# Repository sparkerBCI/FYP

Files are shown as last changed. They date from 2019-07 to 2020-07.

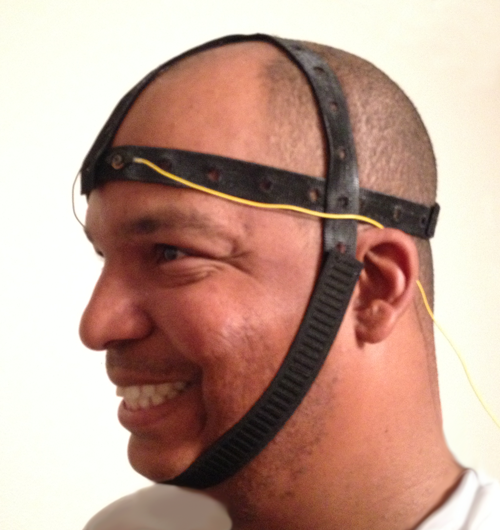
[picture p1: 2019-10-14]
Documentation/Report/Pictures/headstrap.png

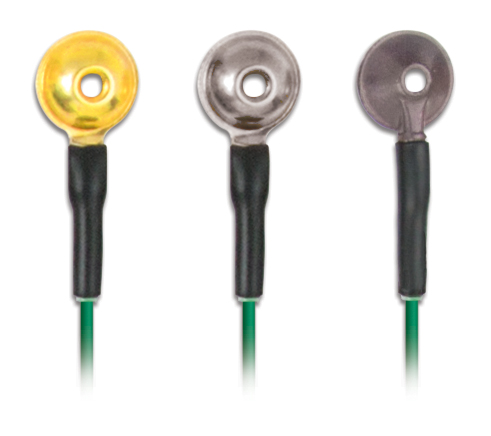
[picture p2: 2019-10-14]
Documentation/Report/Pictures/grass_stamped_eeg_cup_electrodes.jpg

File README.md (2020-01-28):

# Brain Computer Interface Controlled, 3-D Printed Prosthetic Hand

This is an Electrical Engineering Final   Year Project by Samuel Parker, from the University of Newcastle.

### Scope
The project will attempt to conduct a real time frequency analysis of on-line EEG data. The frequency content will then be classified into "Hand Open" or "Hand Closed" using an appropriate classification algorithm. Once classified, the state will be used to control the servos in the 3D printed prosthetic hand. The goal of the project is to achieve realtime, neurally controlled grasping.

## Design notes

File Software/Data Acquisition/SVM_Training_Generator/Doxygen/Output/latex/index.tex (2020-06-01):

\DoxyHorRuler{0}

\begin{DoxyAuthor}{Author}
Sam Parker 
\end{DoxyAuthor}
\begin{DoxyVersion}{Version}
0.\+03
\end{DoxyVersion}
\hypertarget{index_intro_sec}{}\doxysection{Introduction}\label{index_intro_sec}
This is the software for the Sparker Wireless E\+EG Data Acquisition System. It was developed by Sam Parker as part of his Electrical Engineering Final Year Project at the University of Newcastle, Australia. This software contains interface functions to set-\/up, configure, and operate a Texas Instruments A\+D\+S1299 E\+EG Analog Front End device. It then pipes the data to a serial port (U\+SB or Bluetooth).\hypertarget{index_mech}{}\doxysection{Mechanics}\label{index_mech}
The software is relatively simple. It instantiates a Pin\+\_\+\+Map, which tells the device how the pins are mapped. If this software is being run on a board other than the Sparker Data Acquisition System, you need to check the Pin\+\_\+\+Map is still correct. It then uses the Pin\+\_\+\+Map to communicate with the A\+D\+S1299 over an S\+PI interface. The device is configured for the Sparker Data Acquisition board, so if it is to be used with a different recording montage, new data rate, etc. the setup process will need to be altered. Serial communications are managed by the Serial Module, which also has debug, warning, and error messages. These messages should only be used when send data over U\+SB and you will need to check for the ID byte to distinguish between real data ana a message. If communicating over bluetooth, or these messages aren\textquotesingle{}t desired, they can be switched off individually.\hypertarget{index_walkthrough}{}\doxysection{Walkthrough of the Read Process}\label{index_walkthrough}
Assuming your device has been set up correctly (big assumption), the main loop checks to see if the device is running. At this point there is no way to start the device remotely (i.\+e. from the host serial device), but I might add this later if I think it is useful. If the device is running, the status L\+ED will flash. The device will then poll the Data Ready pin until it goes low, when it issues the R\+D\+A\+TA command, which sends 1 sample over the S\+PI interface. The sample ID bits are checked to make sure it\textquotesingle{}s not corrupt, then it\textquotesingle{}s processed and given a sequential sample ID. Sample I\+Ds start at 1, and sample I\+Ds of 0 mean the sample is invalid. But Sam, you say, doesn\textquotesingle{}t that mean that when the Sample I\+Ds overflow a good sample will be read as invalid? Yes it does. But the sample I\+Ds won\textquotesingle{}t overflow for 192 days of continuous recording, and if you\textquotesingle{}re running this thing for 192 days you should use a better D\+AQ system. Valid samples are then sent over the serial interface (38400 baud) in the format (sample ID)(Channel 1)(Channel 2)(Channel 3) ...(Channel 8)(\textbackslash{}n). Everything except the \textbackslash{}n are uint32\+\_\+ts in 8 data bits, no parity, 1 stop bit. Data is sent M\+SB first, most significant byte first. It then polls the Data Ready pin and starts again.

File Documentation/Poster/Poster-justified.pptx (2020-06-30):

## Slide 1

Wireless EEG Controlled Prosthetic

Samuel Parker, Kaushik Mahata

Overview

Many people across the world are living with reduced upper limb function due to a breakdown in their neural signaling pathway. Often the cortical areas responsible for movement remain functional, allowing the signals to be detected and decoded, then the motor intent can be executed using a robotic prosthetic. This is a Brain Computer Interface (BCI) Neuroprosthetic.

Utilising novel feature extraction techniques, cortical signals recorded at the scalp have been used to classify motor intent in real time, enabling the user to grasp objects using the power of thought alone.

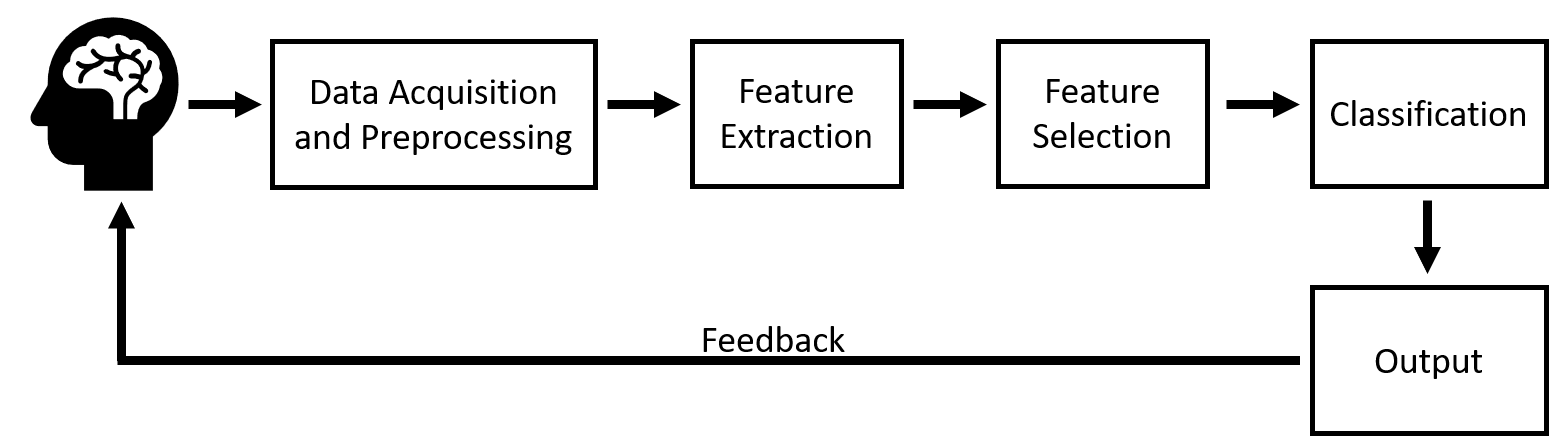
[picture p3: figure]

BCI Fundamentals

Wireless Data Acquisition

Recording cortical activity from the scalp is called electroencephalography (EEG). These signals are very small, and are very sensitive to noise, so specialised hardware is required. This system uses a custom board built on the ADS1299 by Texas Instruments. The signal is then sent using Bluetooth to the arm for further processing.

Novel Feature Extraction

Motor intent is encoded in the firing rates of neurons. This is detected by examining the frequency content of the EEG signals. Applying the Discrete Cosine Transform (DCT), EEG observations could be classified to the same accuracy in 26% of the time taken by benchmark approach (the Short Time Fourier Transform, or STFT). This is extremely exciting for online BCI systems, where classification time is critical.

Embedded SVM Classifier

The Classification and Control Board (based on an STM32F407) receives the EEG signal over Bluetooth and computes the DCT. The extracted features are classified as “Hand Open” or “Hand Closed” using a Support Vector Machine (SVM) machine learning algorithm. The SVM model is created using a training dataset and Matlab, then uploaded to the board. When the SVM has predicted the state of the hand, 5 PWM control signals are generated to control each finger.

80%

Classification Accuracy & Time vs FE Method

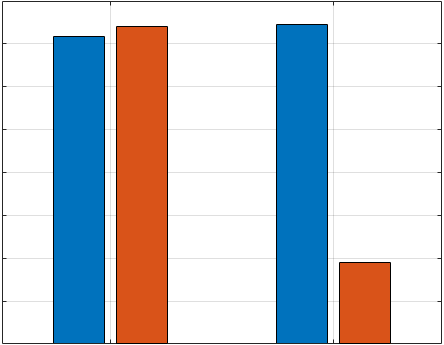
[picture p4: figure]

0.016s

60%

40%

0.012s

0.008s

20%

0%

STFT

DCT

0.004s

0.000s

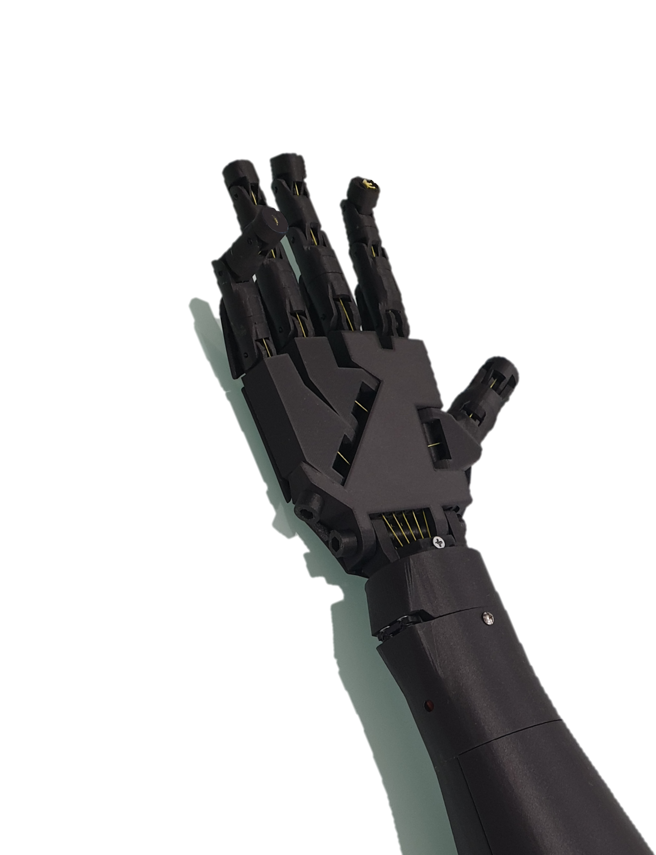
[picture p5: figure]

The 3D Printed Prosthetic Hand

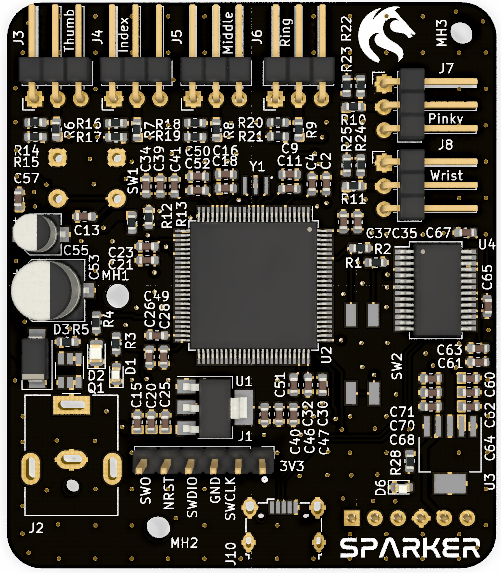
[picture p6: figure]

The Classification &
Control Board

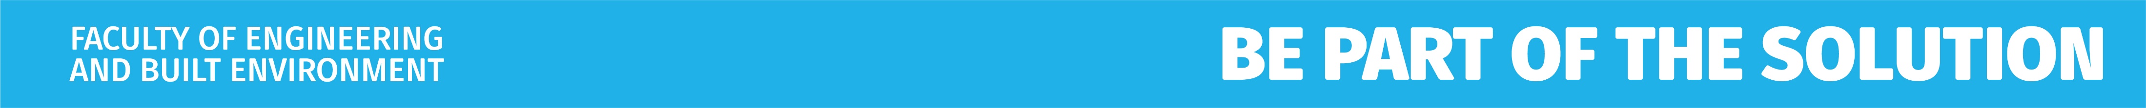
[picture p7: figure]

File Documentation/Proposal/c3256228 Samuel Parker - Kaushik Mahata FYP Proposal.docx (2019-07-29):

Title: | EEG Controlled 3D Printed Prosthetic Hand
Supervisor: | Kaushik Mahata
Level of Difficulty: | ☐ Easy (Pass type project), ☐ Medium Difficulty (Pass to Credit), ☐ Difficult (Credit to Distinction), ☑ Challenging (Distinction to High Distinction).
Assumed knowledge: | ELEC3730, ELEC4410, ELEC3400, ELEC3240, ENGG3500, ELEC3850, ELEC2440
Type of Project: | ☑ Hardware ☑ Software ☐ Simulation ☑ Literature Search
No. of Students: | ☑ Single ☐ Group

Description:

The aim of this project is to design and construct a 3D printed prosthetic hand controlled by decoding neural activity. The device will amplify and filter real-time electroencephalography (EEG) data from an EEG cap, conduct a frequency analysis, then use classification techniques to determine the state of the wearer’s hand (open or closed). This classification will be used to drive the servos in the prosthetic device. This will enable grasping of items such as umbrellas, water bottles, and cutlery, which would have a dramatic effect in the lives of people living with upper limb amputations, spinal cord injuries, or degenerative diseases.

Outcomes Expected:
Real-time neurally controlled grasping. This will be achieved through binary classification of EEG data.

Resources:

- An EEG Cap and electrodes
- A 3D Printed Prosthetic Hand and Wrist
  - STL Files are available in the references section, however electronic components will be required.

References:

https://pdfs.semanticscholar.org/c864/6a15245732a8f91fb74294562b99d19628df.pdf

http://inmoov.fr/hand-and-forarm/

https://ieeexplore.ieee.org/document/6564011

# 1. Scope

## 1.1. Context

Across the globe, thousands of people suffer from upper limb disabilities. These disabilities may be due to amputation, stroke, spinal cord injuries, or degenerative diseases. In many cases, the patients’ motor cortical function remain intact, however due to their condition, the neural signals to not reach their destination with enough integrity to enable the desired action. The solution to this problem is neuroprosthetic devices. These experimental devices decode the neural activity of the patient to enable classification of motor intent. These classifications are then used to control a robotic prosthetic device. Such devices are currently being researched, and with continued endeavor, will be clinically available in our lifetime. A survey conducted by Engdahl et al concluded that participants showed the most interest in simple prosthesis features (such as opening and closing the hand slowly), rather than fine motor control and touch sensation. This indicates that there is a real-world interest in the development of devices similar to that proposed in this project.

## 1.2. Nature of Work

The project will involve:

- Analog Electronics (for filtering and amplification of the EEG signals),
- Embedded System Software Development (for the implementation of an AAR, or SVM classification approach, or similar),
- Signal Processing (to conduct a frequency analysis of the EEG signals),
- Project Management (to ensure all outcomes are met and the project remains on schedule),
- Systems Engineering (to interface the data acquisition and processing modules with the prosthetic), and
- Control Systems (to convert the classification into a joint angle).
  1.3. Relationship to Other Courses Completed

It is anticipated that this project will draw on knowledge developed during:

- ELEC3730 – Digital and Computer Electronics 2
- ELEC3400 – Signal Processing
- ELEC3240 – Analog Electronics
- ENGG3500 – Managing Engineering Projects
- ELEC3850 – Electrical Engineering Design and Practice
- ELEC2440 – Modelling and Control
  1.4. Goals of the Project

The goal of the project is to achieve real-time neurally controlled grasping, by decoding EEG signals to control a 3D printed prosthetic hand.

# 2. Supervision

Dr Kaushik Mahata has graciously agreed to supervise this project.

# 3. Commercial Confidentiality

It is not anticipated that any aspect of this project will be subject to any commercial-in-confidence agreements.

# 4. Intellectual Property

To preserve the student’s ability to pursue subsequent development in this area, the respective contributions of parties involved will be clearly documented.

# 5. Equipment and Consumables

To achieve real-time online processing, an EEG cap would be required. Dry electrodes would be preferred, due to their easier set-up. It is anticipated that an appropriate cap will be sourced by the student, who will then claim a reimbursement from the Final Year Project Budget. Thus, the University will have claim to these items at the completion of the project.

The prosthetic hand and wrist can be 3D printed using the .STL files available to download from inMoov. It is anticipated that the University can 3D print these files. As such, the University would have claim to the printed components at the completion of the project.

Additional electronics such as servos will be claimed under the project budget, so will remain property of the University.

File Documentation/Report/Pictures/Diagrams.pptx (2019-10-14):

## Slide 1

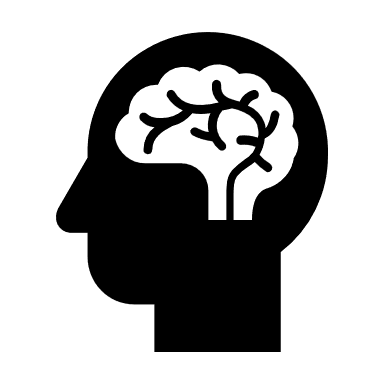
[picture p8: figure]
Brain in head

Data Acquisition and Preprocessing

DCT

Linear SVM

Output

Feedback

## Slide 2

EEG Electrode

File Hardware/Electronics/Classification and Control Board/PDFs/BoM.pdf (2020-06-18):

Ref | Value | Package | Price | SMD | THT | Notes | Digikey Part #
C11 | 10n | Capacitor_SMD:C_0603_1608Metric | $0.17 | 1 | 0 | 10000pF ±10% 50V Ceramic Capacitor X7R 0603 (1608 Metric) | 445-5662-1-ND
C13 | 0.1u | Capacitor_SMD:C_0603_1608Metric | $0.17 | 1 | 0 | 0.1µF ±10% 50V Ceramic Capacitor X7R 0603 (1608 Metric) | 1276-CL10B104KB8NNNLCT-ND
C15 | 4.7u | Capacitor_SMD:C_0603_1608Metric | $0.63 | 1 | 0 | 4.7µF ±10% 25V Ceramic Capacitor X5R 0603 (1608 Metric) | 1276-1900-1-ND
C16 | 100n | Capacitor_SMD:C_0603_1608Metric | $0.17 | 1 | 0 | 0.1µF ±10% 50V Ceramic Capacitor X7R 0603 (1608 Metric) | 1276-CL10B104KB8NNNLCT-ND
C18 | 10n | Capacitor_SMD:C_0603_1608Metric | $0.17 | 1 | 0 | 10000pF ±10% 50V Ceramic Capacitor X7R 0603 (1608 Metric) | 445-5662-1-ND
C2 | 100n | Capacitor_SMD:C_0603_1608Metric | $0.17 | 1 | 0 | 0.1µF ±10% 50V Ceramic Capacitor X7R 0603 (1608 Metric) | 1276-CL10B104KB8NNNLCT-ND
C20 | 10n | Capacitor_SMD:C_0603_1608Metric | $0.17 | 1 | 0 | 10000pF ±10% 50V Ceramic Capacitor X7R 0603 (1608 Metric) | 445-5662-1-ND
C21 | 100n | Capacitor_SMD:C_0603_1608Metric | $0.17 | 1 | 0 | 0.1µF ±10% 50V Ceramic Capacitor X7R 0603 (1608 Metric) | 1276-CL10B104KB8NNNLCT-ND
C23 | 10n | Capacitor_SMD:C_0603_1608Metric | $0.17 | 1 | 0 | 10000pF ±10% 50V Ceramic Capacitor X7R 0603 (1608 Metric) | 445-5662-1-ND
C25 | 1n | Capacitor_SMD:C_0603_1608Metric | $0.17 | 1 | 0 | 1000pF ±10% 50V Ceramic Capacitor X7R 0603 (1608 Metric) | 311-1080-1-ND
C26 | 100n | Capacitor_SMD:C_0603_1608Metric | $0.17 | 1 | 0 | 0.1µF ±10% 50V Ceramic Capacitor X7R 0603 (1608 Metric) | 1276-CL10B104KB8NNNLCT-ND
C28 | 10n | Capacitor_SMD:C_0603_1608Metric | $0.17 | 1 | 0 | 10000pF ±10% 50V Ceramic Capacitor X7R 0603 (1608 Metric) | 445-5662-1-ND
C30 | 100n | Capacitor_SMD:C_0603_1608Metric | $0.17 | 1 | 0 | 0.1µF ±10% 50V Ceramic Capacitor X7R 0603 (1608 Metric) | 1276-CL10B104KB8NNNLCT-ND
C32 | 10n | Capacitor_SMD:C_0603_1608Metric | $0.17 | 1 | 0 | 10000pF ±10% 50V Ceramic Capacitor X7R 0603 (1608 Metric) | 445-5662-1-ND
C34 | 10n | Capacitor_SMD:C_0603_1608Metric | $0.17 | 1 | 0 | 10000pF ±10% 50V Ceramic Capacitor X7R 0603 (1608 Metric) | 445-5662-1-ND
C35 | 100n | Capacitor_SMD:C_0603_1608Metric | $0.17 | 1 | 0 | 0.1µF ±10% 50V Ceramic Capacitor X7R 0603 (1608 Metric) | 1276-CL10B104KB8NNNLCT-ND
C37 | 10n | Capacitor_SMD:C_0603_1608Metric | $0.17 | 1 | 0 | 10000pF ±10% 50V Ceramic Capacitor X7R 0603 (1608 Metric) | 445-5662-1-ND
C39 | 100n | Capacitor_SMD:C_0603_1608Metric | $0.17 | 1 | 0 | 0.1µF ±10% 50V Ceramic Capacitor X7R 0603 (1608 Metric) | 1276-CL10B104KB8NNNLCT-ND
C4 | 10n | Capacitor_SMD:C_0603_1608Metric | $0.17 | 1 | 0 | 10000pF ±10% 50V Ceramic Capacitor X7R 0603 (1608 Metric) | 445-5662-1-ND
C40 | 1n | Capacitor_SMD:C_0603_1608Metric | $0.17 | 1 | 0 | 1000pF ±10% 50V Ceramic Capacitor X7R 0603 (1608 Metric) | 311-1080-1-ND
C41 | 1u | Capacitor_SMD:C_0603_1608Metric | $0.17 | 1 | 0 | 1µF ±20% 16V Ceramic Capacitor X7R 0603 (1608 Metric) | 1276-6524-1-ND
C46 | 10n | Capacitor_SMD:C_0603_1608Metric | $0.17 | 1 | 0 | 10000pF ±10% 50V Ceramic Capacitor X7R 0603 (1608 Metric) | 445-5662-1-ND
C47 | 4.7u | Capacitor_SMD:C_0603_1608Metric | $0.63 | 1 | 0 | 4.7µF ±10% 25V Ceramic Capacitor X5R 0603 (1608 Metric) | 1276-1900-1-ND
C49 | 2.2u | Capacitor_SMD:C_0603_1608Metric | $0.24 | 1 | 0 | 2.2µF ±10% 16V Ceramic Capacitor X5R 0603 (1608 Metric) | 399-7886-1-ND
C50 | 1u | Capacitor_SMD:C_0603_1608Metric | $0.17 | 1 | 0 | 1µF ±20% 16V Ceramic Capacitor X7R 0603 (1608 Metric) | 1276-6524-1-ND
C51 | 2.2u | Capacitor_SMD:C_0603_1608Metric | $0.24 | 1 | 0 | 2.2µF ±10% 16V Ceramic Capacitor X5R 0603 (1608 Metric) | 399-7886-1-ND
C52 | 10n | Capacitor_SMD:C_0603_1608Metric | $0.17 | 1 | 0 | 10000pF ±10% 50V Ceramic Capacitor X7R 0603 (1608 Metric) | 445-5662-1-ND
C53 | 100u | Capacitor_SMD:CP_Elec_6.3x7.7 | $0.80 | 1 | 0 | 100µF 25V Aluminum Electrolytic Capacitors Radial, Can - SMD 2000 Hrs @ 85°C | PCE3898CT-ND
C55 | 10u | Capacitor_SMD:CP_Elec_4x5.4 | $0.46 | 1 | 0 | 10µF 16V Aluminum Electrolytic Capacitors Radial, Can - SMD 2000 Hrs @ 85°C | 493-2100-1-ND
C57 | 4.7u | Capacitor_SMD:C_0603_1608Metric | $0.63 | 1 | 0 | 4.7µF ±10% 25V Ceramic Capacitor X5R 0603 (1608 Metric) | 1276-1900-1-ND
C60 | 4.7u | Capacitor_SMD:C_0603_1608Metric | $0.63 | 1 | 0 | 4.7µF ±10% 25V Ceramic Capacitor X5R 0603 (1608 Metric) | 1276-1900-1-ND
C61 | 100n | Capacitor_SMD:C_0603_1608Metric | $0.17 | 1 | 0 | 0.1µF ±10% 50V Ceramic Capacitor X7R 0603 (1608 Metric) | 1276-CL10B104KB8NNNLCT-ND
C62 | 100n | Capacitor_SMD:C_0603_1608Metric | $0.17 | 1 | 0 | 0.1µF ±10% 50V Ceramic Capacitor X7R 0603 (1608 Metric) | 1276-CL10B104KB8NNNLCT-ND
C63 | 10n | Capacitor_SMD:C_0603_1608Metric | $0.17 | 1 | 0 | 10000pF ±10% 50V Ceramic Capacitor X7R 0603 (1608 Metric) | 445-5662-1-ND
C64 | 10n | Capacitor_SMD:C_0603_1608Metric | $0.17 | 1 | 0 | 10000pF ±10% 50V Ceramic Capacitor X7R 0603 (1608 Metric) | 445-5662-1-ND
C65 | 10n | Capacitor_SMD:C_0603_1608Metric | $0.17 | 1 | 0 | 10000pF ±10% 50V Ceramic Capacitor X7R 0603 (1608 Metric) | 445-5662-1-ND
C67 | 100n | Capacitor_SMD:C_0603_1608Metric | $0.17 | 1 | 0 | 0.1µF ±10% 50V Ceramic Capacitor X7R 0603 (1608 Metric) | 1276-CL10B104KB8NNNLCT-ND
C68 | 4.7u | Capacitor_SMD:C_0603_1608Metric | $0.63 | 1 | 0 | 4.7µF ±10% 25V Ceramic Capacitor X5R 0603 (1608 Metric) | 1276-1900-1-ND
C70 | 100n | Capacitor_SMD:C_0603_1608Metric | $0.17 | 1 | 0 | 0.1µF ±10% 50V Ceramic Capacitor X7R 0603 (1608 Metric) | 1276-CL10B104KB8NNNLCT-ND
C71 | 10n | Capacitor_SMD:C_0603_1608Metric | $0.17 | 1 | 0 | 10000pF ±10% 50V Ceramic Capacitor X7R 0603 (1608 Metric) | 445-5662-1-ND
C9 | 100n | Capacitor_SMD:C_0603_1608Metric | $0.17 | 1 | 0 | 0.1µF ±10% 50V Ceramic Capacitor X7R 0603 (1608 Metric) | 1276-CL10B104KB8NNNLCT-ND
D1 | LTST-C171TGKT | LED_SMD:LED_0805_2012Metric | $0.44 | 1 | 0 | Green 571nm LED Indication - Discrete 2V 0603 (1608 Metric) | 160-1446-1-ND
D2 | LO R976-PS-1 | LED_SMD:LED_0805_2012Metric | $0.47 | 1 | 0 | Orange 606nm LED Indication - Discrete 2V 0805 (2012 Metric) | 475-2488-1-ND
D3 | 10V | Diode_SMD:D_SMA | $0.76 | 1 | 0 | Zener Diode 10V 1W ±5% Surface Mount SMA | SMAZ10-FDICT-ND
D6 | LTST-C171TGKT | LED_SMD:LED_0805_2012Metric | $0.44 | 1 | 0 | Green 571nm LED Indication - Discrete 2V 0603 (1608 Metric) | 160-1446-1-ND
J1 | SWD Header | Connector_PinHeader_2.54mm:PinHeader_1x06_P2.54mm_Vertical | $0.46 | 0 | 1 | Connector Header Through Hole 6 position 0.100" (2.54mm) | 609-3263-ND
J10 | USB_B_Mini | Connector_USB:USB_Micro-B_Wuerth_629105150521 | $3.51 | 1 | 0 | USB - micro B USB 2.0 Receptacle Connector 5 Position Surface Mount, Right Angle; Through Hole | 732-5960-1-ND
J2 | Barrel_Jack | Connector_BarrelJack:BarrelJack_CUI_PJ-063AH_Horizontal | $2.31 | 0 | 1 | Power Barrel Connector Jack 2.10mm ID (0.083"), 5.50mm OD (0.217") Through Hole, Right Angle | CP-063AH-ND
J3 | Thumb | Connector_PinHeader_2.54mm:PinHeader_1x03_P2.54mm_Horizontal | $0.25 | 0 | 1 | Connector Header Through Hole, Right Angle 3 position 0.100" (2.54mm) | 609-6345-ND
J4 | Index | Connector_PinHeader_2.54mm:PinHeader_1x03_P2.54mm_Horizontal | $0.25 | 0 | 1 | Connector Header Through Hole, Right Angle 3 position 0.100" (2.54mm) | 609-6345-ND
J5 | Middle | Connector_PinHeader_2.54mm:PinHeader_1x03_P2.54mm_Horizontal | $0.25 | 0 | 1 | Connector Header Through Hole, Right Angle 3 position 0.100" (2.54mm) | 609-6345-ND
J6 | Ring | Connector_PinHeader_2.54mm:PinHeader_1x03_P2.54mm_Horizontal | $0.25 | 0 | 1 | Connector Header Through Hole, Right Angle 3 position 0.100" (2.54mm) | 609-6345-ND
J7 | Pinky | Connector_PinHeader_2.54mm:PinHeader_1x03_P2.54mm_Horizontal | $0.25 | 0 | 1 | Connector Header Through Hole, Right Angle 3 position 0.100" (2.54mm) | 609-6345-ND
J8 | Wrist | Connector_PinHeader_2.54mm:PinHeader_1x03_P2.54mm_Horizontal | $0.25 | 0 | 1 | Connector Header Through Hole, Right Angle 3 position 0.100" (2.54mm) | 609-6345-ND
J9 | HC05 | Resonators:HC-05 | $1.12 | 0 | 1 | 6 Position Header Connector Through Hole, Right Angle | S5481-ND
LOGO1 | SparkerLogo | Sparker:NASA_small | $0.00 | 0 | 0 | Silkscreen
LOGO2 | UoNLogo | Sparker:UoN | $0.00 | 0 | 0 | Silkscreen
MH1 | MountingHole | MountingHole:MountingHole_2.7mm_M2.5 | $0.00 | 0 | 0 | Mounting Hole
MH2 | MountingHole | MountingHole:MountingHole_2.7mm_M2.5 | $0.00 | 0 | 0 | Mounting Hole
MH3 | MountingHole | MountingHole:MountingHole_2.7mm_M2.5 | $0.00 | 0 | 0 | Mounting Hole
Q1 | SQ3425EV-T1_GE3 | Package_TO_SOT_SMD:TSOT-23-6 | $1.07 | 1 | 0 | P-Channel 20V 7.4A (Tc) 5W (Tc) Surface Mount 6-TSOP | SQ3425EV-T1_GE3CT-ND
R1 | 100k | Resistor_SMD:R_0603_1608Metric | $0.58 | 1 | 0 | 100 kOhms ±0.1% 0.1W, 1/10W Chip Resistor 0603 (1608 Metric) Automotive AEC-Q200 Thin Film | P100KDBCT-ND
R10 | 50m | Resistor_SMD:R_0603_1608Metric | $0.68 | 1 | 0 | 50 mOhms ±0.5% 0.2W, 1/5W Chip Resistor 0603 (1608 Metric) Current Sense Metal Film | 273-KDV06DR050ETCT-ND
R11 | 50m | Resistor_SMD:R_0603_1608Metric | $0.68 | 1 | 0 | 50 mOhms ±0.5% 0.2W, 1/5W Chip Resistor 0603 (1608 Metric) Current Sense Metal Film | 273-KDV06DR050ETCT-ND
R12 | 500k | Resistor_SMD:R_0603_1608Metric | $0.29 | 1 | 0 | 499 kOhms ±1% 0.333W, 1/3W Chip Resistor 0603 (1608 Metric) Automotive AEC-Q200, Pulse Withstanding Thick Film | 541-499KSCT-ND
R13 | 100k | Resistor_SMD:R_0603_1608Metric | $0.58 | 1 | 0 | 100 kOhms ±0.1% 0.1W, 1/10W Chip Resistor 0603 (1608 Metric) Automotive AEC-Q200 Thin Film | P100KDBCT-ND
R14 | 500k | Resistor_SMD:R_0603_1608Metric | $0.29 | 1 | 0 | 499 kOhms ±1% 0.333W, 1/3W Chip Resistor 0603 (1608 Metric) Automotive AEC-Q200, Pulse Withstanding Thick Film | 541-499KSCT-ND
R15 | 100k | Resistor_SMD:R_0603_1608Metric | $0.58 | 1 | 0 | 100 kOhms ±0.1% 0.1W, 1/10W Chip Resistor 0603 (1608 Metric) Automotive AEC-Q200 Thin Film | P100KDBCT-ND
R16 | 500k | Resistor_SMD:R_0603_1608Metric | $0.29 | 1 | 0 | 499 kOhms ±1% 0.333W, 1/3W Chip Resistor 0603 (1608 Metric) Automotive AEC-Q200, Pulse Withstanding Thick Film | 541-499KSCT-ND
R17 | 100k | Resistor_SMD:R_0603_1608Metric | $0.58 | 1 | 0 | 100 kOhms ±0.1% 0.1W, 1/10W Chip Resistor 0603 (1608 Metric) Automotive AEC-Q200 Thin Film | P100KDBCT-ND
R18 | 500k | Resistor_SMD:R_0603_1608Metric | $0.29 | 1 | 0 | 499 kOhms ±1% 0.333W, 1/3W Chip Resistor 0603 (1608 Metric) Automotive AEC-Q200, Pulse Withstanding Thick Film | 541-499KSCT-ND
R19 | 100k | Resistor_SMD:R_0603_1608Metric | $0.58 | 1 | 0 | 100 kOhms ±0.1% 0.1W, 1/10W Chip Resistor 0603 (1608 Metric) Automotive AEC-Q200 Thin Film | P100KDBCT-ND

R2 | 100k | Resistor_SMD:R_0603_1608Metric | $0.58 | 1 | 0 | 100 kOhms ±0.1% 0.1W, 1/10W Chip Resistor 0603 (1608 Metric) Automotive AEC-Q200 Thin Film | P100KDBCT-ND
R20 | 500k | Resistor_SMD:R_0603_1608Metric | $0.29 | 1 | 0 | 499 kOhms ±1% 0.333W, 1/3W Chip Resistor 0603 (1608 Metric) Automotive AEC-Q200, Pulse Withstanding Thick Film | 541-499KSCT-ND
R21 | 100k | Resistor_SMD:R_0603_1608Metric | $0.58 | 1 | 0 | 100 kOhms ±0.1% 0.1W, 1/10W Chip Resistor 0603 (1608 Metric) Automotive AEC-Q200 Thin Film | P100KDBCT-ND
R22 | 500k | Resistor_SMD:R_0603_1608Metric | $0.29 | 1 | 0 | 499 kOhms ±1% 0.333W, 1/3W Chip Resistor 0603 (1608 Metric) Automotive AEC-Q200, Pulse Withstanding Thick Film | 541-499KSCT-ND
R23 | 100k | Resistor_SMD:R_0603_1608Metric | $0.58 | 1 | 0 | 100 kOhms ±0.1% 0.1W, 1/10W Chip Resistor 0603 (1608 Metric) Automotive AEC-Q200 Thin Film | P100KDBCT-ND
R24 | 500k | Resistor_SMD:R_0603_1608Metric | $0.29 | 1 | 0 | 499 kOhms ±1% 0.333W, 1/3W Chip Resistor 0603 (1608 Metric) Automotive AEC-Q200, Pulse Withstanding Thick Film | 541-499KSCT-ND
R25 | 100k | Resistor_SMD:R_0603_1608Metric | $0.58 | 1 | 0 | 100 kOhms ±0.1% 0.1W, 1/10W Chip Resistor 0603 (1608 Metric) Automotive AEC-Q200 Thin Film | P100KDBCT-ND
R28 | 150 | Resistor_SMD:R_0603_1608Metric | $0.17 | 1 | 0 | 150 Ohms ±5% 0.25W, 1/4W Chip Resistor 0603 (1608 Metric) Automotive AEC-Q200, Pulse Withstanding Thick Film | RHM150DCT-ND
R3 | 6R | Resistor_SMD:R_0603_1608Metric | $0.31 | 1 | 0 | 6.8 Ohms ±1% 0.1W, 1/10W Chip Resistor 0603 (1608 Metric) Automotive AEC-Q200, Current Sense Thick Film | P6.8AJCT-ND
R4 | 68R | Resistor_SMD:R_0603_1608Metric | $0.29 | 1 | 0 | 68 Ohms ±1% 0.333W, 1/3W Chip Resistor 0603 (1608 Metric) Automotive AEC-Q200, Pulse Withstanding Thick Film | 541-68.0SCT-ND
R5 | 33k | Resistor_SMD:R_0603_1608Metric | $0.25 | 1 | 0 | 33 kOhms ±1% 0.25W, 1/4W Chip Resistor 0603 (1608 Metric) Pulse Withstanding Thick Film | A130434CT-ND
R6 | 50m | Resistor_SMD:R_0603_1608Metric | $0.68 | 1 | 0 | 50 mOhms ±0.5% 0.2W, 1/5W Chip Resistor 0603 (1608 Metric) Current Sense Metal Film | 273-KDV06DR050ETCT-ND
R7 | 50m | Resistor_SMD:R_0603_1608Metric | $0.68 | 1 | 0 | 50 mOhms ±0.5% 0.2W, 1/5W Chip Resistor 0603 (1608 Metric) Current Sense Metal Film | 273-KDV06DR050ETCT-ND
R8 | 50m | Resistor_SMD:R_0603_1608Metric | $0.68 | 1 | 0 | 50 mOhms ±0.5% 0.2W, 1/5W Chip Resistor 0603 (1608 Metric) Current Sense Metal Film | 273-KDV06DR050ETCT-ND
R9 | 50m | Resistor_SMD:R_0603_1608Metric | $0.68 | 1 | 0 | 50 mOhms ±0.5% 0.2W, 1/5W Chip Resistor 0603 (1608 Metric) Current Sense Metal Film | 273-KDV06DR050ETCT-ND
SW1 | SW_Push | Switches:1825910-6 | $0.00 | 0 | 1 | Tactile Switch SPST-NO Top Actuated Through Hole | 450-1650-ND
SW2 | SW_DIP_x02 | Switches:DIP-Switch_01x02 | $0.00 | 1 | 0 | Dip Switch SPST 2 Position Surface Mount Slide (Standard) Actuator 100mA 20VDC | CT3113CT-ND
U1 | LDL1117S33R | Package_TO_SOT_SMD:SOT-223-3_TabPin2 | $0.73 | 1 | 0 | Linear Voltage Regulator IC 1 Output 1.2A SOT-223 | 497-17239-1-ND
U2 | STM32F407VGTx | Package_QFP:LQFP-100_14x14mm_P0.5mm | $0.00 | 1 | 0 | ARM® Cortex®-M4 STM32F4 Microcontroller IC 32-Bit 168MHz 1MB (1M x 8) FLASH 100-LQFP (14x14) | 497-17437-1-ND
U3 | MCP1755T-5002E_SOT223-5 | Package_TO_SOT_SMD:SOT-223-6 | $0.00 | 1 | 0 | Linear Voltage Regulator IC 1 Output 300mA SOT-223-5 | MCP1755T-5002E/DCCT-ND
U4 | FT232RL | Package_SO:SSOP-28_5.3x10.2mm_P0.65mm | $7.63 | 1 | 0 | USB Bridge, USB to UART USB 2.0 UART Interface 28-SSOP | 768-1007-1-ND
Y1 | 8MHz | Resonators:CSTNE12M0GH5L000R0 | $0.47 | 1 | 0 | 8MHz Ceramic Resonator Built in Capacitor 33pF ±0.2% 40 Ohms -40°C ~ 85°C Surface Mount | 490-17958-1-ND
| | Total | $43.59

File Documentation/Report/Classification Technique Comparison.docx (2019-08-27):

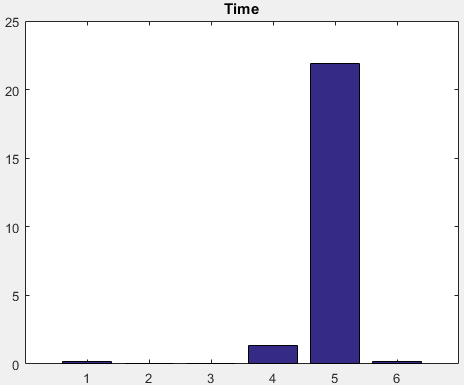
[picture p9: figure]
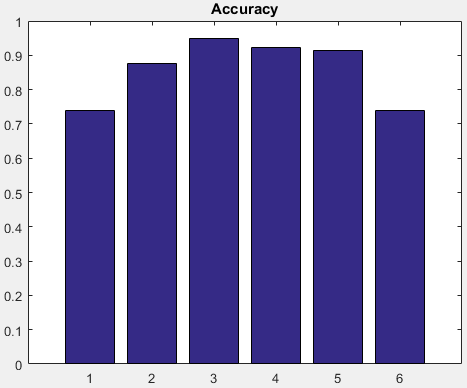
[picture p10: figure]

# Classification Technique Comparison

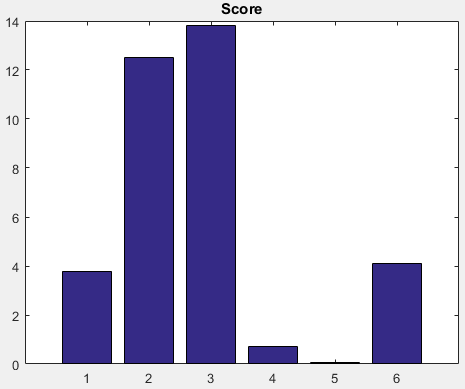
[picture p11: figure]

1. Gaussian SVM
2. Linear SVM
3. RBF SVM
4. Polynomial SVM
5. LDA
6. KNN

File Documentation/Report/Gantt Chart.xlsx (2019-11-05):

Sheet: ProjectSchedule
Create a Project Schedule in this worksheet. Enter title of this project in cell B1. Information about how to use this worksheet, including instructions for screen readers and the author of this workbook is in the About worksheet. Continue navigating down column A to hear further instructions. | Gantt Chart for Project Completion
Enter Company Name in cell B2. | BCI Prosthetic
Enter the name of the Project Lead in cell B3. Enter the Project Start date in cell E3. Pooject Start: label is in cell C3. | Samuel Parker | 2019-11-26
The Display Week in cell E4 represents the starting week to display in the project schedule in cell I4. The project start date is considered Week 1. To change the display week, simply enter a new week number in cell E4. The starting date for each week, starting with the display week from cell E4, starts in cell I4 and is auto calculated. There are 8 weeks represented in this view from cell I4 through cell BF4. You should not modify these cells. Display Week: label is in cell C4. |  | 1 |  | 2019-11-25 |  |  |  |  |  |  | 2019-12-02 |  |  |  |  |  |  | 2019-12-09 |  |  |  |  |  |  | 2019-12-16 |  |  |  |  |  |  | 2019-12-23 |  |  |  |  |  |  | 2019-12-30 |  |  |  |  |  |  | 2020-01-06 |  |  |  |  |  |  | 2020-01-13
Cells I5 through BL5 contain the day number for the week represented in the cell block above each date cell and are auto calculated. You should not modify these cells. Today's date is outlined in Red (hex #AD3815) from today's date in row 5 through the entire date column to the end of the project schedule. |  |  |  | 2019-11-25 | 2019-11-26 | 2019-11-27 | 2019-11-28 | 2019-11-29 | 2019-11-30 | 2019-12-01 | 2019-12-02 | 2019-12-03 | 2019-12-04 | 2019-12-05 | 2019-12-06 | 2019-12-07 | 2019-12-08 | 2019-12-09 | 2019-12-10 | 2019-12-11 | 2019-12-12 | 2019-12-13 | 2019-12-14 | 2019-12-15 | 2019-12-16 | 2019-12-17 | 2019-12-18 | 2019-12-19 | 2019-12-20 | 2019-12-21 | 2019-12-22 | 2019-12-23 | 2019-12-24 | 2019-12-25 | 2019-12-26 | 2019-12-27 | 2019-12-28 | 2019-12-29 | 2019-12-30 | 2019-12-31 | 2020-01-01 | 2020-01-02 | 2020-01-03 | 2020-01-04 | 2020-01-05 | 2020-01-06 | 2020-01-07 | 2020-01-08 | 2020-01-09 | 2020-01-10 | 2020-01-11 | 2020-01-12 | 2020-01-13 | 2020-01-14 | 2020-01-15 | 2020-01-16 | 2020-01-17
This row contains headers for the project schedule that follows below them. Navigate from B6 through BL 6 to hear the content. The first letter of each day of the week for the date above that heading, starts in cell I6 and continues through cell BL6. All project timeline charting is auto generated based on the start and end dates entered, using conditional formats. Do not modify content in cells within columns after column I starting with cell I7. | TASK | START | END | M | T | W | T | F | S | S | M | T | W | T | F | S | S | M | T | W | T | F | S | S | M | T | W | T | F | S | S | M | T | W | T | F | S | S | M | T | W | T | F | S | S | M | T | W | T | F | S | S | M | T | W | T | F
Cell B8 contains the Phase 1 sample title. Enter a new Title in cell B8. Enter a name to assign the phase to, if it applies for your project, in cell C8. Enter Progress for the entire phase, if it applies for your project, in cell D8. Enter the start and end dates for the entire phase, if it applies for your project, in cells E8 and F8. The Gantt chart will automatically fill in the appropriate dates and shade according to the progress entered. To delete the phase and work only from tasks, simply delete this row. | EEG Hardware Procurement
Cell B9 contains the sample task "Task 1." Enter a new task name in cell B9. Enter a person to assign the task to in cell C9. Enter progres of the task in cell D9. A progress bar appears in the cell and is shaded according to the number in the cell. For example, 50 percent progress would shade half of the cell. Enter task start date in cell E9. Enter task end date in cell F9. A status bar shaded for the dates entered appears in blocks starting from cell I9 through BL9. | Procurement | 2019-11-26 | 2020-01-11
The cell at right contains the Phase 2 sample title. You can create a new phase at any time within column B. This project schedule does not require phases. To remove the phase, simply delete the row. To create a new phase block in this row, enter a new Title in cell at right. To continue adding tasks to the phase above, enter a new row above this one and fill in the task data as in cell A9's instruction. Update the Phase details in cell at right based on cell A8's instruction. Continue navigating down column A cells to learn more. If you haven't added any new rows in this worksheet, you will find 2 additional sample phase blocks have been created for you in cells B20 and B26. Otherwise, navigate through column A cells to find the additional blocks. Repeat the instructions from cells A8 and A9 whenever you need to. | Data Acquisition System
 | Final PCB Review | 2019-11-26 | 2019-11-28
 | Submit Fab Order | 2019-11-28 | 2019-11-28
 | Component Procurement | 2019-11-28 | 2019-12-07
 | Board Delivery | 2019-11-28 | 2019-12-07
 | Assembly | 2019-12-07 | 2019-12-20
 | Software | 2019-12-07 | 2019-12-20
 | Testing | 2019-12-20 | 2020-01-16
Sample phase title block | Classification and Control System
 | Schematic Drawing | 2019-11-26 | 2019-12-09
 | PCB Layout | 2019-12-10 | 2019-12-16
 | PCB Review | 2019-12-17 | 2019-12-30
 | Submit Fab Order | 2019-12-31 | 2019-12-31
 | Component Procurement | 2019-12-31 | 2020-01-09
 | Board Delivery | 2019-12-31 | 2020-01-09
 | Assembly | 2020-01-10 | 2020-01-23
 | Software | 2020-01-10 | 2020-02-21
 | Testing | 2020-02-22 | 2020-03-13
Sample phase title block | System Integration
 | Physical Integration | 2020-03-14 | 2020-03-15
 | Interface Testing | 2020-03-15 | 2020-03-21
 | Full System Testing | 2020-03-22 | 2020-04-21
 | Finalising Demonstration | 2020-04-22 | 2020-05-02
Sample phase title block | (Optional) Scope Expansion
 | Spatial Filtering Feasability Study | 2020-05-03 | 2020-05-17
 | Finger Control Scheme Feasability Study | 2020-05-03 | 2020-05-17
 | Additional System Development | 2020-05-18 | 2020-06-17
 | Finalising Demonstration | 2020-06-18 | 2020-06-23
Sample phase title block | Documentation
 | Classification and Control Hardware | 2019-12-31 | 2020-01-14
 | Classification and Control Documentation | 2019-12-31 | 2020-01-14
 | Gathering Results | 2019-12-20 | 2020-05-02
 | Evaluating Results | 2020-05-03 | 2020-05-17
 | Acknowledgements & Contributions | 2020-05-18 | 2020-05-19
 | Poster | 2020-05-18 | 2020-06-02
This is an empty row
This row marks the end of the Project Schedule. DO NOT enter anything in this row. Insert new rows ABOVE this one to continue building out your Project Schedule. | Insert new rows ABOVE this one

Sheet: About
SIMPLE GANTT CHART by Vertex42.com (https://www.vertex42.com/ExcelTemplates/simple-gantt-chart.html)
https://www.vertex42.com/ExcelTemplates/simple-gantt-chart.html
About This Template
This template provides a simple way to create a Gantt chart to help visualize and track your project. Simply enter your tasks and start and end dates - no formulas required. The bars in the Gantt chart represent the duration of the task and are displayed using conditional formatting. Insert new tasks by inserting new rows.
Guide for Screen Readers
There are 2 worksheets in this workbook. TimeSheet About The instructions for each worksheet are in the A column starting in cell A1 of each worksheet. They are written with hidden text. Each step guides you through the information in that row. Each subsequent step continues in cell A2, A3, and so on, unless otherwise explicitly directed. For example, instruction text might say "continue to cell A6" for the next step. This hidden text will not print. To remove these instructions from the worksheet, simply delete column A.
Additional Help
Click on the link below to visit vertex42.com and learn more about how to use this template, such as how to calculate days and work days, create task dependencies, change the colors of the bars, add a scroll bar to make it easier to change the display week, extend the date range displayed in the chart, etc.
How to Use the Simple Gantt Chart (https://www.vertex42.com/ExcelTemplates/simple-gantt-chart.html)
More Project Management Templates
Visit Vertex42.com to download other project management templates, including different types of project schedules, Gantt charts, tasks lists, etc.
Project Management Templates (https://www.vertex42.com/ExcelTemplates/excel-project-management.html)
About Vertex42
Vertex42.com provides over 300 professionally designed spreadsheet templates for business, home, and education - most of which are free to download. Their collection includes a variety of calendars, planners, and schedules as well as personal finance spreadsheets for budgeting, debt reduction, and loan amortization.
Businesses will find invoices, time sheets, inventory trackers, financial statements, and project planning templates. Teachers and students will find resources such as class schedules, grade books, and attendance sheets. Organize your family life with meal planners, checklists, and exercise logs. Each template is thoroughly researched, refined, and improved over time through feedback from thousands of users.
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

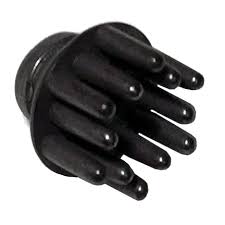
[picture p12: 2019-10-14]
Documentation/Report/Pictures/dry.jpg

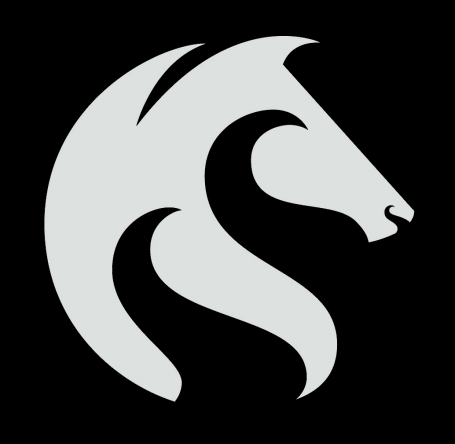
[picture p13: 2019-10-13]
Hardware/Electronics/Pictures/UoN.bmp

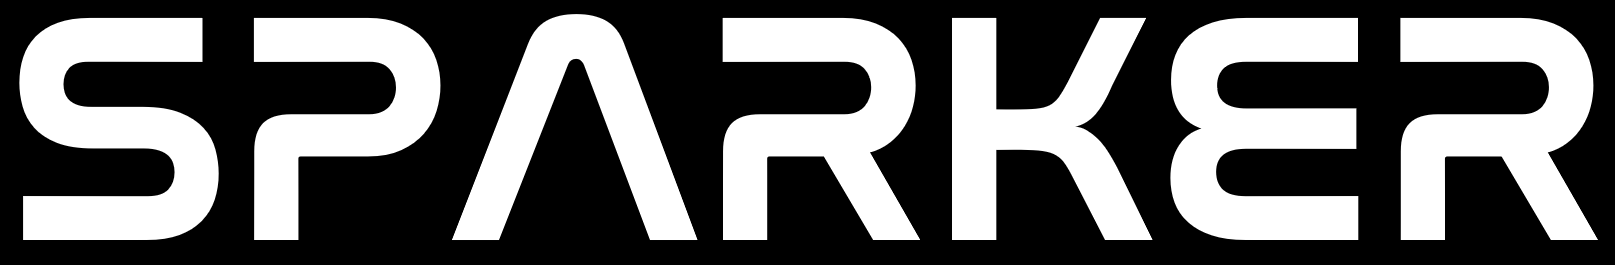
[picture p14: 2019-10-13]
Hardware/Electronics/Pictures/NASA.PNG

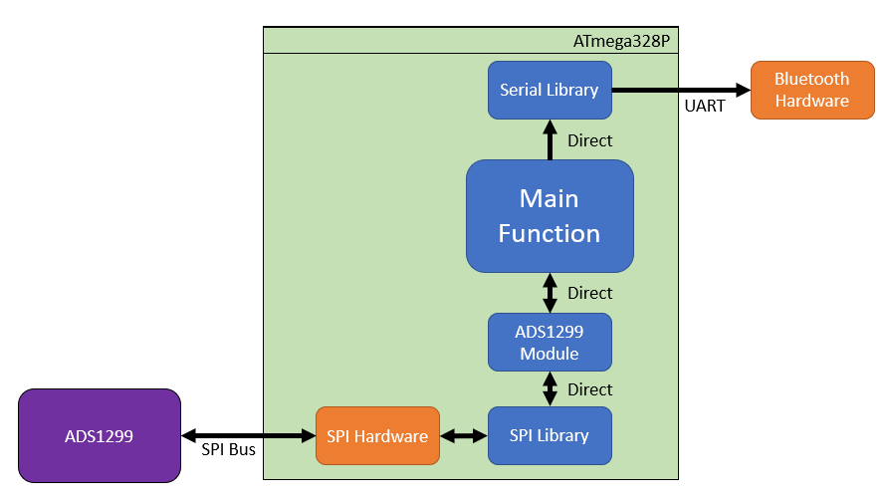
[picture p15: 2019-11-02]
Documentation/Report/Pictures/Data Acquisition Software.PNG

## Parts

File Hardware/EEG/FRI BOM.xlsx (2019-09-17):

 | USD | AUD | QTY | TOTAL | Notes
Pack of 10 Electrodes and Leads | $83.95 | $122.57 |  | $0.00 | Price per electrode | $12.26 | AUD
Pack of 5 Electrodes and Leads | $48.95 | $71.47 | 1 | $71.47 | Price per electrode | $14.29 | AUD
Pack of 3 Electrodes and Leads | $34.95 | $51.03 |  | $0.00 | Price per electrode | $17.01 | AUD
Pack of 10 Electrodes | $7.00 | $10.22 |  | $0.00
Basic Headband Set | $70.00 | $102.20 |  | $0.00 | 15 Dry Electrodes, 10 Wet Electrodes, Headband, 5 Leads
Delux Headband Set | $115.00 | $167.90 |  | $0.00 | 20 Dry Electrodes, 20 Wet Electrodes, Headband, 10 Leads
Ear Clip | $20.00 | $29.20 | 1 | $29.20
Lead | $8.15 | $11.90 |  | $0.00
Headband | $30.00 | $43.80 | 1 | $43.80
 |  |  | TOTAL | $144.47
 | USD | AUD | QTY | TOTAL | Notes
Pack of 10 Electrodes and Leads | $83.95 | $122.57 |  | $0.00 | Price per electrode | $12.26 | AUD
Pack of 5 Electrodes and Leads | $48.95 | $71.47 |  | $0.00 | Price per electrode | $14.29 | AUD
Pack of 3 Electrodes and Leads | $34.95 | $51.03 |  | $0.00 | Price per electrode | $17.01 | AUD
Pack of 10 Electrodes | $7.00 | $10.22 |  | $0.00
Basic Headband Set | $70.00 | $102.20 | 1 | $102.20 | 15 Dry Electrodes, 10 Wet Electrodes, Headband, 5 Leads
Delux Headband Set | $115.00 | $167.90 | 0 | $0.00 | 20 Dry Electrodes, 20 Wet Electrodes, Headband, 10 Leads
Ear Clip | $20.00 | $29.20 | 1 | $29.20
Lead | $8.15 | $11.90 |  | $0.00
Headband | $30.00 | $43.80 |  | $0.00
19 Channel Headband | $50.00 | $73.00 |  | $0.00
 |  |  | TOTAL | $131.40

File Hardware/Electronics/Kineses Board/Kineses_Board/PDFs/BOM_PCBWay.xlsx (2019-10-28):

 |  |  | xxxx xxxx xxxxx 1PCS BOM (Sample Bill of Materials)
Item # | *Ref Des | *Qty | Manufacturer | *Mfg Part # | Description / Value | *Package | Type | Your Instructions / Notes
1 | A1 | 1 | Arduino | Arduino Nano | Microcontroller | Nonstandard | THT | DO NOT PLACE, DO NOT SUPPLY
2 | C1 | 1 | Panasonic Electronic Components | EEE-1AA101WR | 100µF 10V Aluminum Electrolytic Capacitors Radial, Can - SMD 1000 Hrs @ 85°C | Radial, Can - SMD | SMD
3 | C2 | 1 | Samsung Electro-Mechanics | CL05A106MP8NUB8 | 10µF ±20% 10V Ceramic Capacitor X5R 0402 (1005 Metric) | 0402 | SMD
4 | C3 | 1 | Samsung Electro-Mechanics | CL05F104ZO5NNNC | 0.1µF -20%, +80% 16V Ceramic Capacitor Y5V (F) 0402 (1005 Metric) | 0402 | SMD
5 | C4 | 1 | Yageo | CC0402KRX7R7BB103 | 10000pF ±10% 16V Ceramic Capacitor X7R 0402 (1005 Metric) | 0402 | SMD
6 | J1 | 1 | Adam Tech | PH1RB-02-UA | Connector Header Through Hole, Right Angle 2 position 0.100" (2.54mm) | - | THT | Any manufacturer is OK
7 | J2, J3, J4, J5, J6, J7 | 6 | Amphenol ICC (FCI) | 68000-203HLF | Connector Header Through Hole 3 position 0.100" (2.54mm) | - | THT | Any manufacturer is OK
13 | J8 | 1 | Amphenol ICC (FCI) | 68000-406HLF | Connector Header Through Hole 6 position 0.100" (2.54mm) | - | THT | DO NOT PLACE
14 | LOGO1, LOGO2 | 1 | - | - | Silkscreen Logo | - | - | Silkscreen
15 | MH1, MH2 | 1 | - | - | Mounting Hole | - | THT
16 | R1 | 1 | Yageo | RT0402BRD072KL | 2 kOhms ±0.1% 0.063W, 1/16W Chip Resistor 0402 (1005 Metric) Thin Film | 0402 | SMD
17 | R2 | 1 | Yageo | RT0402FRE071KL | 1 kOhms ±1% 0.063W, 1/16W Chip Resistor 0402 (1005 Metric) Thin Film | 0402 | SMD

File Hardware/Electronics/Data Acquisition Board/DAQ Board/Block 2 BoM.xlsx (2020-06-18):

Ref | Value | Package | Price | SMD | THT | Notes | Digikey Part #
ADC1 | ADS1299-8 | Package_QFP:TQFP-64_10x10mm_P0.5mm | $86.98 | 1 | 0 | 8 Channel AFE 24 Bit 42mW 64-TQFP (10x10) | 296-34818-1-ND
C1 | 24nF | Capacitor_SMD:C_0805_2012Metric | $0.82 | 1 | 0 | 0.022µF ±5% 50V Ceramic Capacitor C0G, NP0 0805 (2012 Metric) | 490-1644-1-ND
C2 | 24nF | Capacitor_SMD:C_0805_2012Metric | $0.82 | 1 | 0 | 0.022µF ±5% 50V Ceramic Capacitor C0G, NP0 0805 (2012 Metric) | 490-1644-1-ND
C3 | 24nF | Capacitor_SMD:C_0805_2012Metric | $0.82 | 1 | 0 | 0.022µF ±5% 50V Ceramic Capacitor C0G, NP0 0805 (2012 Metric) | 490-1644-1-ND
C4 | 24nF | Capacitor_SMD:C_0805_2012Metric | $0.82 | 1 | 0 | 0.022µF ±5% 50V Ceramic Capacitor C0G, NP0 0805 (2012 Metric) | 490-1644-1-ND
C5 | 24nF | Capacitor_SMD:C_0805_2012Metric | $0.82 | 1 | 0 | 0.022µF ±5% 50V Ceramic Capacitor C0G, NP0 0805 (2012 Metric) | 490-1644-1-ND
C6 | 24nF | Capacitor_SMD:C_0805_2012Metric | $0.82 | 1 | 0 | 0.022µF ±5% 50V Ceramic Capacitor C0G, NP0 0805 (2012 Metric) | 490-1644-1-ND
C7 | 24nF | Capacitor_SMD:C_0805_2012Metric | $0.82 | 1 | 0 | 0.022µF ±5% 50V Ceramic Capacitor C0G, NP0 0805 (2012 Metric) | 490-1644-1-ND
C8 | 24nF | Capacitor_SMD:C_0805_2012Metric | $0.82 | 1 | 0 | 0.022µF ±5% 50V Ceramic Capacitor C0G, NP0 0805 (2012 Metric) | 490-1644-1-ND
C9 | 1uF | Capacitor_SMD:C_0603_1608Metric | $0.17 | 1 | 0 | 1µF ±20% 16V Ceramic Capacitor X7R 0603 (1608 Metric) | 1276-6524-1-ND
C10 | 1uF | Capacitor_SMD:C_0603_1608Metric | $0.17 | 1 | 0 | 1µF ±20% 16V Ceramic Capacitor X7R 0603 (1608 Metric) | 1276-6524-1-ND
C12 | 0.1uF | Capacitor_SMD:C_0603_1608Metric | $0.17 | 1 | 0 | 0.1µF ±10% 50V Ceramic Capacitor X7R 0603 (1608 Metric) | 1276-CL10B104KB8NNNLCT-ND
C13 | 10uF | Capacitor_SMD:C_0603_1608Metric | $0.28 | 1 | 0 | 10µF ±20% 6.3V Ceramic Capacitor X5R 0603 (1608 Metric) | 1276-1119-1-ND
C14 | 1uF | Capacitor_SMD:C_0603_1608Metric | $0.17 | 1 | 0 | 1µF ±20% 16V Ceramic Capacitor X7R 0603 (1608 Metric) | 1276-6524-1-ND
C15 | 0.1uF | Capacitor_SMD:C_0603_1608Metric | $0.17 | 1 | 0 | 0.1µF ±10% 50V Ceramic Capacitor X7R 0603 (1608 Metric) | 1276-CL10B104KB8NNNLCT-ND
C16 | 100uF | Capacitor_SMD:C_1206_3216Metric | $2.60 | 1 | 0 | 100µF ±20% 10V Ceramic Capacitor X5R 1206 (3216 Metric) | 445-6007-1-ND
C17 | 1uF | Capacitor_SMD:C_0603_1608Metric | $0.17 | 1 | 0 | 1µF ±20% 16V Ceramic Capacitor X7R 0603 (1608 Metric) | 1276-6524-1-ND
C18 | 1uF | Capacitor_SMD:C_0603_1608Metric | $0.17 | 1 | 0 | 1µF ±20% 16V Ceramic Capacitor X7R 0603 (1608 Metric) | 1276-6524-1-ND
C19 | 1uF | Capacitor_SMD:C_0603_1608Metric | $0.17 | 1 | 0 | 1µF ±20% 16V Ceramic Capacitor X7R 0603 (1608 Metric) | 1276-6524-1-ND
C20 | 0.1uF | Capacitor_SMD:C_0603_1608Metric | $0.17 | 1 | 0 | 0.1µF ±10% 50V Ceramic Capacitor X7R 0603 (1608 Metric) | 1276-CL10B104KB8NNNLCT-ND
C21 | 1uF | Capacitor_SMD:C_0603_1608Metric | $0.17 | 1 | 0 | 1µF ±20% 16V Ceramic Capacitor X7R 0603 (1608 Metric) | 1276-6524-1-ND
C22 | 100nF | Capacitor_SMD:C_0603_1608Metric | $0.17 | 1 | 0 | 0.1µF ±10% 50V Ceramic Capacitor X7R 0603 (1608 Metric) | 1276-CL10B104KB8NNNLCT-ND
C23 | 1uF | Capacitor_SMD:C_0603_1608Metric | $0.17 | 1 | 0 | 1µF ±20% 16V Ceramic Capacitor X7R 0603 (1608 Metric) | 1276-6524-1-ND
C24 | 4.7uF | Capacitor_SMD:C_0603_1608Metric | $0.58 | 1 | 0 | 4.7µF ±10% 25V Ceramic Capacitor X5R 0603 (1608 Metric) | 1276-1900-1-ND
C25 | 1uF | Capacitor_SMD:C_0603_1608Metric | $0.17 | 1 | 0 | 1µF ±20% 16V Ceramic Capacitor X7R 0603 (1608 Metric) | 1276-6524-1-ND
C26 | 100uF | Capacitor_SMD:C_1206_3216Metric | $2.60 | 1 | 0 | 100µF ±20% 10V Ceramic Capacitor X5R 1206 (3216 Metric) | 445-6007-1-ND
C27 | 10uF | Capacitor_SMD:C_0603_1608Metric | $0.28 | 1 | 0 | 10µF ±20% 6.3V Ceramic Capacitor X5R 0603 (1608 Metric) | 1276-1119-1-ND
C28 | 100uF | Capacitor_SMD:C_1206_3216Metric | $2.60 | 1 | 0 | 100µF ±20% 10V Ceramic Capacitor X5R 1206 (3216 Metric) | 445-6007-1-ND
C29 | 100nF | Capacitor_SMD:C_0603_1608Metric | $0.17 | 1 | 0 | 0.1µF ±10% 50V Ceramic Capacitor X7R 0603 (1608 Metric) | 1276-CL10B104KB8NNNLCT-ND
C30 | 10uF | Capacitor_SMD:C_0603_1608Metric | $0.28 | 1 | 0 | 10µF ±20% 6.3V Ceramic Capacitor X5R 0603 (1608 Metric) | 1276-1119-1-ND
C31 | 10nF | Capacitor_SMD:C_0603_1608Metric | $0.17 | 1 | 0 | 10000pF ±10% 50V Ceramic Capacitor X7R 0603 (1608 Metric) | 445-5662-1-ND
C32 | 100nF | Capacitor_SMD:C_0603_1608Metric | $0.17 | 1 | 0 | 0.1µF ±10% 50V Ceramic Capacitor X7R 0603 (1608 Metric) | 1276-CL10B104KB8NNNLCT-ND
C33 | 10nF | Capacitor_SMD:C_0603_1608Metric | $0.17 | 1 | 0 | 10000pF ±10% 50V Ceramic Capacitor X7R 0603 (1608 Metric) | 445-5662-1-ND
C34 | 1nF | Capacitor_SMD:C_0603_1608Metric | $0.16 | 1 | 0 | 1000pF ±10% 50V Ceramic Capacitor X7R 0603 (1608 Metric) | 311-1080-1-ND
C35 | 10nF | Capacitor_SMD:C_0603_1608Metric | $0.17 | 1 | 0 | 10000pF ±10% 50V Ceramic Capacitor X7R 0603 (1608 Metric) | 445-5662-1-ND
C36 | 1nF | Capacitor_SMD:C_0603_1608Metric | $0.16 | 1 | 0 | 1000pF ±10% 50V Ceramic Capacitor X7R 0603 (1608 Metric) | 311-1080-1-ND
C37 | 100nF | Capacitor_SMD:C_0603_1608Metric | $0.17 | 1 | 0 | 0.1µF ±10% 50V Ceramic Capacitor X7R 0603 (1608 Metric) | 1276-CL10B104KB8NNNLCT-ND
C38 | 10nF | Capacitor_SMD:C_0603_1608Metric | $0.17 | 1 | 0 | 10000pF ±10% 50V Ceramic Capacitor X7R 0603 (1608 Metric) | 445-5662-1-ND
C39 | 10uF | Capacitor_SMD:C_0603_1608Metric | $0.28 | 1 | 0 | 10µF ±20% 6.3V Ceramic Capacitor X5R 0603 (1608 Metric) | 1276-1119-1-ND
C40 | 100nF | Capacitor_SMD:C_0603_1608Metric | $0.17 | 1 | 0 | 0.1µF ±10% 50V Ceramic Capacitor X7R 0603 (1608 Metric) | 1276-CL10B104KB8NNNLCT-ND
C41 | 10uF | Capacitor_SMD:C_0603_1608Metric | $0.28 | 1 | 0 | 10µF ±20% 6.3V Ceramic Capacitor X5R 0603 (1608 Metric) | 1276-1119-1-ND
C42 | 100uF | Capacitor_SMD:C_1206_3216Metric | $2.60 | 1 | 0 | 100µF ±20% 10V Ceramic Capacitor X5R 1206 (3216 Metric) | 445-6007-1-ND
C43 | 10uF | Capacitor_SMD:C_0603_1608Metric | $0.28 | 1 | 0 | 10µF ±20% 6.3V Ceramic Capacitor X5R 0603 (1608 Metric) | 1276-1119-1-ND
C44 | 100uF | Capacitor_SMD:C_1206_3216Metric | $2.60 | 1 | 0 | 100µF ±20% 10V Ceramic Capacitor X5R 1206 (3216 Metric) | 445-6007-1-ND
C45 | 10uF | Capacitor_SMD:C_0603_1608Metric | $0.28 | 1 | 0 | 10µF ±20% 6.3V Ceramic Capacitor X5R 0603 (1608 Metric) | 1276-1119-1-ND
C46 | 100nF | Capacitor_SMD:C_0603_1608Metric | $0.17 | 1 | 0 | 0.1µF ±10% 50V Ceramic Capacitor X7R 0603 (1608 Metric) | 1276-CL10B104KB8NNNLCT-ND
C47 | 10nF | Capacitor_SMD:C_0603_1608Metric | $0.17 | 1 | 0 | 10000pF ±10% 50V Ceramic Capacitor X7R 0603 (1608 Metric) | 445-5662-1-ND
C48 | 1nF | Capacitor_SMD:C_0603_1608Metric | $0.16 | 1 | 0 | 1000pF ±10% 50V Ceramic Capacitor X7R 0603 (1608 Metric) | 311-1080-1-ND
C49 | 10nF | Capacitor_SMD:C_0603_1608Metric | $0.17 | 1 | 0 | 10000pF ±10% 50V Ceramic Capacitor X7R 0603 (1608 Metric) | 445-5662-1-ND
C50 | 100nF | Capacitor_SMD:C_0603_1608Metric | $0.17 | 1 | 0 | 0.1µF ±10% 50V Ceramic Capacitor X7R 0603 (1608 Metric) | 1276-CL10B104KB8NNNLCT-ND
C51 | 10uF | Capacitor_SMD:C_0603_1608Metric | $0.28 | 1 | 0 | 10µF ±20% 6.3V Ceramic Capacitor X5R 0603 (1608 Metric) | 1276-1119-1-ND
C52 | 4.7uF | Capacitor_SMD:C_0603_1608Metric | $0.58 | 1 | 0 | 4.7µF ±10% 25V Ceramic Capacitor X5R 0603 (1608 Metric) | 1276-1900-1-ND
C53 | 100nF | Capacitor_SMD:C_0603_1608Metric | $0.17 | 1 | 0 | 0.1µF ±10% 50V Ceramic Capacitor X7R 0603 (1608 Metric) | 1276-CL10B104KB8NNNLCT-ND
C54 | 100nF | Capacitor_SMD:C_0603_1608Metric | $0.17 | 1 | 0 | 0.1µF ±10% 50V Ceramic Capacitor X7R 0603 (1608 Metric) | 1276-CL10B104KB8NNNLCT-ND
C55 | 10uF | Capacitor_SMD:C_0603_1608Metric | $0.28 | 1 | 0 | 10µF ±20% 6.3V Ceramic Capacitor X5R 0603 (1608 Metric) | 1276-1119-1-ND
C56 | 100nF | Capacitor_SMD:C_0603_1608Metric | $0.17 | 1 | 0 | 0.1µF ±10% 50V Ceramic Capacitor X7R 0603 (1608 Metric) | 1276-CL10B104KB8NNNLCT-ND
C57 | 10nF | Capacitor_SMD:C_0603_1608Metric | $0.17 | 1 | 0 | 10000pF ±10% 50V Ceramic Capacitor X7R 0603 (1608 Metric) | 445-5662-1-ND
C58 | 10nF | Capacitor_SMD:C_0603_1608Metric | $0.17 | 1 | 0 | 10000pF ±10% 50V Ceramic Capacitor X7R 0603 (1608 Metric) | 445-5662-1-ND
C59 | 100nF | Capacitor_SMD:C_0603_1608Metric | $0.17 | 1 | 0 | 0.1µF ±10% 50V Ceramic Capacitor X7R 0603 (1608 Metric) | 1276-CL10B104KB8NNNLCT-ND
C60 | 100nF | Capacitor_SMD:C_0603_1608Metric | $0.17 | 1 | 0 | 0.1µF ±10% 50V Ceramic Capacitor X7R 0603 (1608 Metric) | 1276-CL10B104KB8NNNLCT-ND
C61 | 10uF | Capacitor_SMD:C_0603_1608Metric | $0.28 | 1 | 0 | 10µF ±20% 6.3V Ceramic Capacitor X5R 0603 (1608 Metric) | 1276-1119-1-ND
C62 | 10uF | Capacitor_SMD:C_0603_1608Metric | $0.28 | 1 | 0 | 10µF ±20% 6.3V Ceramic Capacitor X5R 0603 (1608 Metric) | 1276-1119-1-ND
C63 | 100n | Capacitor_SMD:C_0603_1608Metric | $0.17 | 1 | 0 | 0.1µF ±10% 50V Ceramic Capacitor X7R 0603 (1608 Metric) | 1276-CL10B104KB8NNNLCT-ND
C64 | 10n | Capacitor_SMD:C_0603_1608Metric | $0.17 | 1 | 0 | 10000pF ±10% 50V Ceramic Capacitor X7R 0603 (1608 Metric) | 445-5662-1-ND
C65 | 10n | Capacitor_SMD:C_0603_1608Metric | $0.17 | 1 | 0 | 10000pF ±10% 50V Ceramic Capacitor X7R 0603 (1608 Metric) | 445-5662-1-ND
C66 | 100n | Capacitor_SMD:C_0603_1608Metric | $0.17 | 1 | 0 | 0.1µF ±10% 50V Ceramic Capacitor X7R 0603 (1608 Metric) | 1276-CL10B104KB8NNNLCT-ND
D3 | 7.5V | Diode_SMD:D_SMA | $0.72 | 1 | 0 | Zener Diode 7.5V 1.5W ±5% Surface Mount SMA | 1SMA5922BT3GOSCT-ND
D4 | LTST-C194TBKT | LED_SMD:LED_0603_1608Metric | $0.70 | 1 | 0 | Blue 468nm LED Indication - Discrete 3.3V 0603 (1608 Metric) | 160-1837-1-ND
D5 | LTST-C191KGKT | LED_SMD:LED_0603_1608Metric | $0.41 | 1 | 0 | Green 571nm LED Indication - Discrete 2V 0603 (1608 Metric) | 160-1446-1-ND
D6 | LTST-C194TBKT | LED_SMD:LED_0603_1608Metric | $0.70 | 1 | 0 | Blue 468nm LED Indication - Discrete 3.3V 0603 (1608 Metric) | 160-1837-1-ND
D7 | B130-13-F | Diode_SMD:D_SMA | $0.55 | 1 | 0 | Diode Schottky 30V 1A Surface Mount SMA | B130-FDICT-ND
D8 | LTST-C191KRKT | LED_SMD:LED_0603_1608Metric | $0.43 | 1 | 0 | Red 631nm LED Indication - Discrete 2V 0603 (1608 Metric) | 160-1447-1-ND
D9 | LTST-C191KGKT | LED_SMD:LED_0603_1608Metric | $0.41 | 1 | 0 | Green 571nm LED Indication - Discrete 2V 0603 (1608 Metric) | 160-1446-1-ND
F1 | 025101.5MAT1L | Resistor_THT:R_Axial_DIN0309_L9.0mm_D3.2mm_P12.70mm_Horizontal | $1.41 | 0 | 1 | 1.5A 125V AC 125V DC Fuse Board Mount (Cartridge Style Excluded) Through Hole Axial | F2319-ND
F2 | MF-MSMF050-2 | Fuse:Fuse_1812_4532Metric | $0.78 | 1 | 0 | Polymeric PTC Resettable Fuse 15V 500mA Ih Surface Mount 1812 (4532 Metric), Concave | MF-MSMF050-2CT-ND
J1 | Conn_01x01_Male | Sparker:DIN 42802-1 | $4.15 | 0 | 1 | Touch-protected Ø 1.5 mm Panelmounting Receptacles (DIN 42802) | (RSOnline) 409-3911
J2 | USB_B_Mini | Connector_USB:USB_Micro-B_Wuerth_629105150521 | $3.44 | 1 | 0 | USB - micro B USB 2.0 Receptacle Connector 5 Position Surface Mount, Right Angle; Through Hole | 732-5960-1-ND
J3 | Conn_01x01_Male | Sparker:DIN 42802-1 | $4.15 | 0 | 1 | Touch-protected Ø 1.5 mm Panelmounting Receptacles (DIN 42802) | (RSOnline) 409-3911
J4 | DC Barrel Jack | Connector_BarrelJack:BarrelJack_CUI_PJ-063AH_Horizontal | $2.15 | 0 | 1 | Power Barrel Connector Jack 2.10mm ID (0.083"), 5.50mm OD (0.217") Through Hole, Right Angle | CP-063AH-ND
J5 | HC-05 BT Module | Resonators:HC-05 | $13.20 | 0 | 1 | Bluetooth Module (HC-05) | (Core) CE00021
J6 | ICSP Header | Connector_PinHeader_2.54mm:PinHeader_2x03_P2.54mm_Vertical | $0.72 | 0 | 1 | Connector Header Through Hole 6 position 0.100" (2.54mm) | 609-3210-ND
J7 | VIN_RAW_TP | Connector_PinHeader_2.54mm:PinHeader_1x02_P2.54mm_Vertical | $0.00 | 0 | 1 | 2.5mm Pin Header Snip Off | NA
J8 | Conn_01x01_Male | Sparker:DIN 42802-1 | $4.15 | 0 | 1 | Touch-protected Ø 1.5 mm Panelmounting Receptacles (DIN 42802) | (RSOnline) 409-3911
J9 | Conn_01x01_Male | Sparker:DIN 42802-1 | $4.15 | 0 | 1 | Touch-protected Ø 1.5 mm Panelmounting Receptacles (DIN 42802) | (RSOnline) 409-3911
J10 | ~CS~_TP | Connector_PinHeader_2.54mm:PinHeader_1x02_P2.54mm_Vertical | $0.00 | 0 | 1 | 2.5mm Pin Header Snip Off | NA
J11 | Conn_01x01_Male | Sparker:DIN 42802-1 | $4.15 | 0 | 1 | Touch-protected Ø 1.5 mm Panelmounting Receptacles (DIN 42802) | (RSOnline) 409-3911
J12 | START_TP | Connector_PinHeader_2.54mm:PinHeader_1x02_P2.54mm_Vertical | $0.00 | 0 | 1 | 2.5mm Pin Header Snip Off | NA
J13 | Conn_01x01_Male | Sparker:DIN 42802-1 | $4.15 | 0 | 1 | Touch-protected Ø 1.5 mm Panelmounting Receptacles (DIN 42802) | (RSOnline) 409-3911
J14 | VREFP_TP | Connector_PinHeader_2.54mm:PinHeader_1x02_P2.54mm_Vertical | $0.00 | 0 | 1 | 2.5mm Pin Header Snip Off | NA
J15 | VCAP1_TP | Connector_PinHeader_2.54mm:PinHeader_1x02_P2.54mm_Vertical | $0.00 | 0 | 1 | 2.5mm Pin Header Snip Off | NA
J16 | DRDY_TP | Connector_PinHeader_2.54mm:PinHeader_1x02_P2.54mm_Vertical | $0.00 | 0 | 1 | 2.5mm Pin Header Snip Off | NA
J17 | Conn_01x01_Male | Sparker:DIN 42802-1 | $4.15 | 0 | 1 | Touch-protected Ø 1.5 mm Panelmounting Receptacles (DIN 42802) | (RSOnline) 409-3911
J18 | Conn_01x01_Male | Sparker:DIN 42802-1 | $4.15 | 0 | 1 | Touch-protected Ø 1.5 mm Panelmounting Receptacles (DIN 42802) | (RSOnline) 409-3911
J19 | Conn_01x01_Male | Sparker:DIN 42802-1 | $4.15 | 0 | 1 | Touch-protected Ø 1.5 mm Panelmounting Receptacles (DIN 42802) | (RSOnline) 409-3911
LOGO1 | UoNLogo | Sparker:UoN |  | 0 | 0
LOGO2 | SparkerLogo | Sparker:NASA |  | 0 | 0
LOGO3 | VersionLogo | Sparker:Block2 |  | 0 | 0
MH1 | MountingHole | MountingHole:MountingHole_3.2mm_M3 |  | 0 | 0
MH2 | MountingHole | MountingHole:MountingHole_3.2mm_M3 |  | 0 | 0
MH3 | MountingHole | MountingHole:MountingHole_3.2mm_M3 |  | 0 | 0
MH4 | MountingHole | MountingHole:MountingHole_3.2mm_M3 |  | 0 | 0
PB1 | TE-1825910-6 | Switches:1825910-6 | $0.16 | 0 | 1 | Tactile Switch SPST-NO Top Actuated Through Hole | 450-1650-ND
Q1 | DMP2100U | Package_TO_SOT_SMD:SOT-23 | $0.67 | 1 | 0 | P-Channel 20V 4.3A (Ta) 800mW (Ta) Surface Mount SOT-23 | DMP2100U-7CT-ND
R3 | 220k | Resistor_SMD:R_0603_1608Metric | $0.58 | 1 | 0 | 220 kOhms ±0.1% 0.1W, 1/10W Chip Resistor 0603 (1608 Metric) Automotive AEC-Q200 Thin Film | P220KDBCT-ND
R4 | 220k | Resistor_SMD:R_0603_1608Metric | $0.58 | 1 | 0 | 220 kOhms ±0.1% 0.1W, 1/10W Chip Resistor 0603 (1608 Metric) Automotive AEC-Q200 Thin Film | P220KDBCT-ND
R5 | 220k | Resistor_SMD:R_0603_1608Metric | $0.58 | 1 | 0 | 220 kOhms ±0.1% 0.1W, 1/10W Chip Resistor 0603 (1608 Metric) Automotive AEC-Q200 Thin Film | P220KDBCT-ND
R6 | 220k | Resistor_SMD:R_0603_1608Metric | $0.58 | 1 | 0 | 220 kOhms ±0.1% 0.1W, 1/10W Chip Resistor 0603 (1608 Metric) Automotive AEC-Q200 Thin Film | P220KDBCT-ND
R7 | 220k | Resistor_SMD:R_0603_1608Metric | $0.58 | 1 | 0 | 220 kOhms ±0.1% 0.1W, 1/10W Chip Resistor 0603 (1608 Metric) Automotive AEC-Q200 Thin Film | P220KDBCT-ND
R8 | 220k | Resistor_SMD:R_0603_1608Metric | $0.58 | 1 | 0 | 220 kOhms ±0.1% 0.1W, 1/10W Chip Resistor 0603 (1608 Metric) Automotive AEC-Q200 Thin Film | P220KDBCT-ND
R9 | 220k | Resistor_SMD:R_0603_1608Metric | $0.58 | 1 | 0 | 220 kOhms ±0.1% 0.1W, 1/10W Chip Resistor 0603 (1608 Metric) Automotive AEC-Q200 Thin Film | P220KDBCT-ND
R10 | 220k | Resistor_SMD:R_0603_1608Metric | $0.58 | 1 | 0 | 220 kOhms ±0.1% 0.1W, 1/10W Chip Resistor 0603 (1608 Metric) Automotive AEC-Q200 Thin Film | P220KDBCT-ND
R11 | 220k | Resistor_SMD:R_0603_1608Metric | $0.58 | 1 | 0 | 220 kOhms ±0.1% 0.1W, 1/10W Chip Resistor 0603 (1608 Metric) Automotive AEC-Q200 Thin Film | P220KDBCT-ND
R12 | 33k | Resistor_SMD:R_0603_1608Metric | $0.54 | 1 | 0 | 33 kOhms ±0.1% 0.1W, 1/10W Chip Resistor 0603 (1608 Metric) Automotive AEC-Q200 Thin Film | P33KDBCT-ND
R13 | 33k | Resistor_SMD:R_0603_1608Metric | $0.54 | 1 | 0 | 33 kOhms ±0.1% 0.1W, 1/10W Chip Resistor 0603 (1608 Metric) Automotive AEC-Q200 Thin Film | P33KDBCT-ND
R14 | 33k | Resistor_SMD:R_0603_1608Metric | $0.57 | 1 | 0 | 33 kOhms ±0.1% 0.1W, 1/10W Chip Resistor 0603 (1608 Metric) Automotive AEC-Q200 Thin Film | P33KDBCT-ND
R15 | 33k | Resistor_SMD:R_0603_1608Metric | $0.57 | 1 | 0 | 33 kOhms ±0.1% 0.1W, 1/10W Chip Resistor 0603 (1608 Metric) Automotive AEC-Q200 Thin Film | P33KDBCT-ND
R16 | 1K | Resistor_SMD:R_0603_1608Metric | $0.17 | 1 | 0 | 1 kOhms ±5% 0.25W, 1/4W Chip Resistor 0603 (1608 Metric) Automotive AEC-Q200, Pulse Withstanding Thick Film | RHM1.0KDCT-ND
R17 | 1K | Resistor_SMD:R_0603_1608Metric | $0.17 | 1 | 0 | 1 kOhms ±5% 0.25W, 1/4W Chip Resistor 0603 (1608 Metric) Automotive AEC-Q200, Pulse Withstanding Thick Film | RHM1.0KDCT-ND
R18 | 1K | Resistor_SMD:R_0603_1608Metric | $0.17 | 1 | 0 | 1 kOhms ±5% 0.25W, 1/4W Chip Resistor 0603 (1608 Metric) Automotive AEC-Q200, Pulse Withstanding Thick Film | RHM1.0KDCT-ND
R19 | 33k | Resistor_SMD:R_0603_1608Metric | $0.57 | 1 | 0 | 33 kOhms ±0.1% 0.1W, 1/10W Chip Resistor 0603 (1608 Metric) Automotive AEC-Q200 Thin Film | P33KDBCT-ND
R20 | 2K | Resistor_SMD:R_0603_1608Metric | $1.05 | 1 | 0 | 2 kOhms ±0.1% 0.1W, 1/10W Chip Resistor 0603 (1608 Metric) Anti-Sulfur Thin Film | 749-1706-1-ND
R21 | 1K | Resistor_SMD:R_0603_1608Metric | $0.17 | 1 | 0 | 1 kOhms ±5% 0.25W, 1/4W Chip Resistor 0603 (1608 Metric) Automotive AEC-Q200, Pulse Withstanding Thick Film | RHM1.0KDCT-ND
R22 | 100 | Resistor_SMD:R_0603_1608Metric | $0.17 | 1 | 0 | 100 Ohms ±5% 0.25W, 1/4W Chip Resistor 0603 (1608 Metric) Automotive AEC-Q200, Pulse Withstanding Thick Film | RHM100DCT-ND
R23 | 100 | Resistor_SMD:R_0603_1608Metric | $0.17 | 1 | 0 | 100 Ohms ±5% 0.25W, 1/4W Chip Resistor 0603 (1608 Metric) Automotive AEC-Q200, Pulse Withstanding Thick Film | RHM100DCT-ND
R24 | 100 | Resistor_SMD:R_0603_1608Metric | $0.17 | 1 | 0 | 100 Ohms ±5% 0.25W, 1/4W Chip Resistor 0603 (1608 Metric) Automotive AEC-Q200, Pulse Withstanding Thick Film | RHM100DCT-ND
R25 | 100 | Resistor_SMD:R_0603_1608Metric | $0.17 | 1 | 0 | 100 Ohms ±5% 0.25W, 1/4W Chip Resistor 0603 (1608 Metric) Automotive AEC-Q200, Pulse Withstanding Thick Film | RHM100DCT-ND
R26 | 100 | Resistor_SMD:R_0603_1608Metric | $0.17 | 1 | 0 | 100 Ohms ±5% 0.25W, 1/4W Chip Resistor 0603 (1608 Metric) Automotive AEC-Q200, Pulse Withstanding Thick Film | RHM100DCT-ND
R27 | 100k | Resistor_SMD:R_0603_1608Metric | $0.22 | 1 | 0 | 100 kOhms ±1% 0.25W, 1/4W Chip Resistor 0603 (1608 Metric) Automotive AEC-Q200, Pulse Withstanding Thick Film | RHM100KADCT-ND
R28 | 100k | Resistor_SMD:R_0603_1608Metric | $0.22 | 1 | 0 | 100 kOhms ±1% 0.25W, 1/4W Chip Resistor 0603 (1608 Metric) Automotive AEC-Q200, Pulse Withstanding Thick Film | RHM100KADCT-ND
SW3 | SW_SPDT | Switches:SPDT-THT_Slide | $1.03 | 0 | 1 | Slide Switch SPDT Through Hole | EG1903-ND
SW4 | SW_SPDT | Switches:SPDT-THT_Slide | $1.03 | 0 | 1 | Slide Switch SPDT Through Hole | EG1903-ND
SW5 | SW_SPDT | Switches:SPDT-THT_Slide | $1.03 | 0 | 1 | Slide Switch SPDT Through Hole | EG1903-ND
SW6 | SW_SPDT | Switches:SPDT-THT_Slide | $1.03 | 0 | 1 | Slide Switch SPDT Through Hole | EG1903-ND
SW7 | SW_SPDT | Switches:SPDT-THT_Slide | $1.03 | 0 | 1 | Slide Switch SPDT Through Hole | EG1903-ND
SW8 | SW_SPDT | Switches:SPDT-THT_Slide | $1.03 | 0 | 1 | Slide Switch SPDT Through Hole | EG1903-ND
SW9 | SW_SPDT | Switches:SPDT-THT_Slide | $1.03 | 0 | 1 | Slide Switch SPDT Through Hole | EG1903-ND
SW10 | SW_SPDT | Switches:SPDT-THT_Slide | $1.03 | 0 | 1 | Slide Switch SPDT Through Hole | EG1903-ND
SW11 | SW_SPDT | Switches:SPDT-THT_Slide | $1.03 | 0 | 1 | Slide Switch SPDT Through Hole | EG1903-ND
U1 | ATmega328P-AU | Package_QFP:TQFP-32_7x7mm_P0.8mm | $2.12 | 1 | 0 | AVR AVR® ATmega Microcontroller IC 8-Bit 20MHz 32KB (16K x 16) FLASH 32-TQFP (7x7) | ATMEGA328PB-AU-ND
U2 | MCP1755T-5002E_SOT223-5 | Package_TO_SOT_SMD:SOT-223-6 | $1.03 | 1 | 0 | Linear Voltage Regulator IC 1 Output 300mA SOT-223-5 | MCP1755T-5002E/DCCT-ND
U3 | LM3480-3.3 | Package_TO_SOT_SMD:SOT-23 | $1.65 | 1 | 0 | Linear Voltage Regulator IC 1 Output 100mA SOT-23-3 | LM3480IM3-3.3/NOPBCT-ND
U4 | MCP1755T-5002E_SOT223-5 | Package_TO_SOT_SMD:SOT-223-6 | $1.03 | 1 | 0 | Linear Voltage Regulator IC 1 Output 300mA SOT-223-5 | MCP1755T-5002E/DCCT-ND
U5 | FT232RL | Package_SO:SSOP-28_5.3x10.2mm_P0.65mm | $7.11 | 1 | 0 | USB Bridge, USB to UART USB 2.0 UART Interface 28-SSOP | 768-1007-1-ND
U6 | TXS0108EPWR | Package_SO:TSSOP-20_4.4x6.5mm_P0.65mm | $2.15 | 1 | 0 | Voltage Level Translator Bidirectional 1 Circuit 8 Channel 60Mbps 20-TSSOP | 296-23011-1-ND
Y1 | 16MHz | Resonators:CSTNE16M0V53Z000R0 | $0.52 | 1 | 0 | 16MHz Ceramic Resonator Built in Capacitor 15pF ±0.3% 40 Ohms -40°C ~ 125°C Surface Mount | 490-17950-1-ND
 |  | Total | $217.09

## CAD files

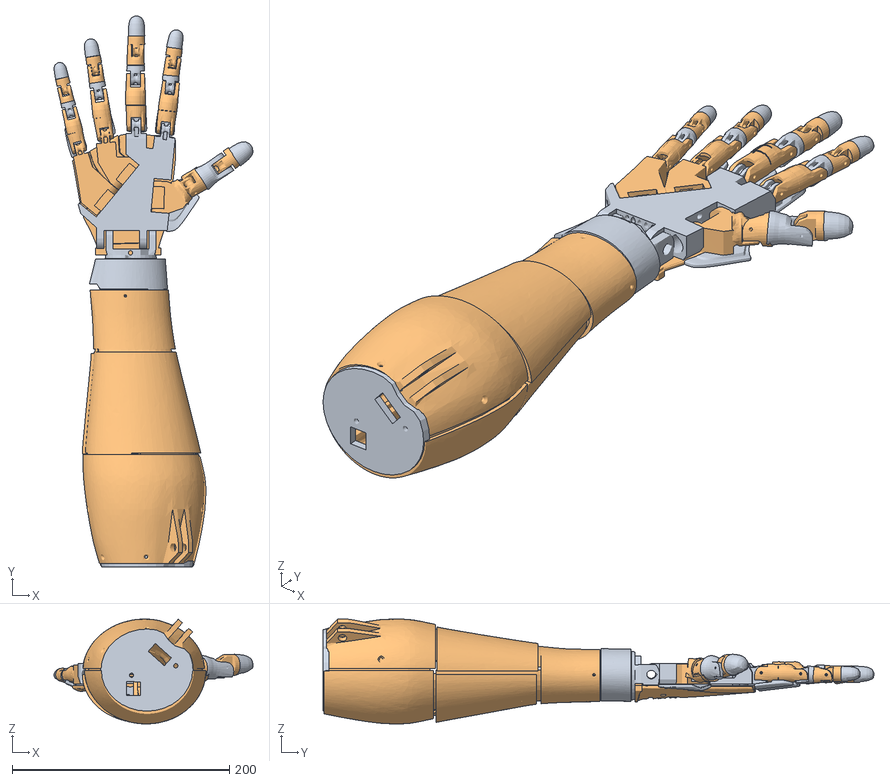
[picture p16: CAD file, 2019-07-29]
Hardware/Prosthetic/InMoovHand.obj
183.1 x 507.1 x 96.5

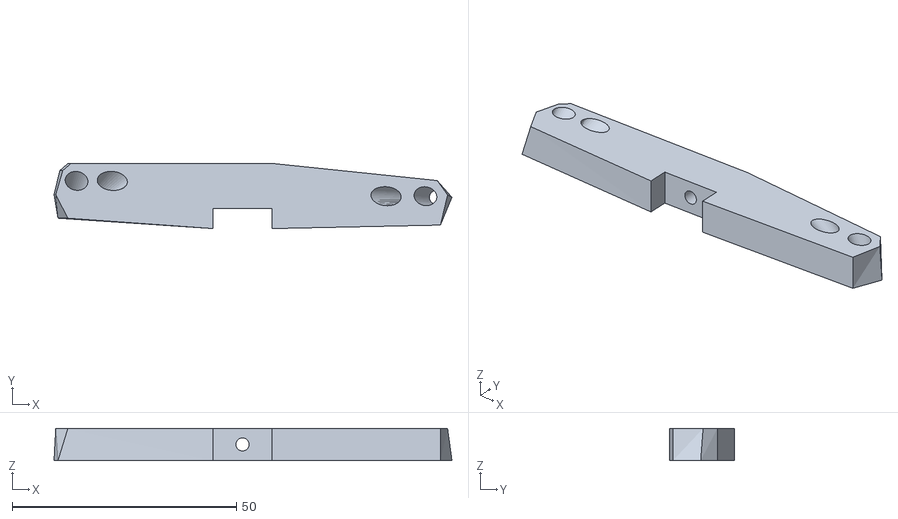
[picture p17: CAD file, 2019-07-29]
Hardware/Prosthetic/Right Forearm/RobCableBackV3.stl
88.7 x 14.5 x 7.17

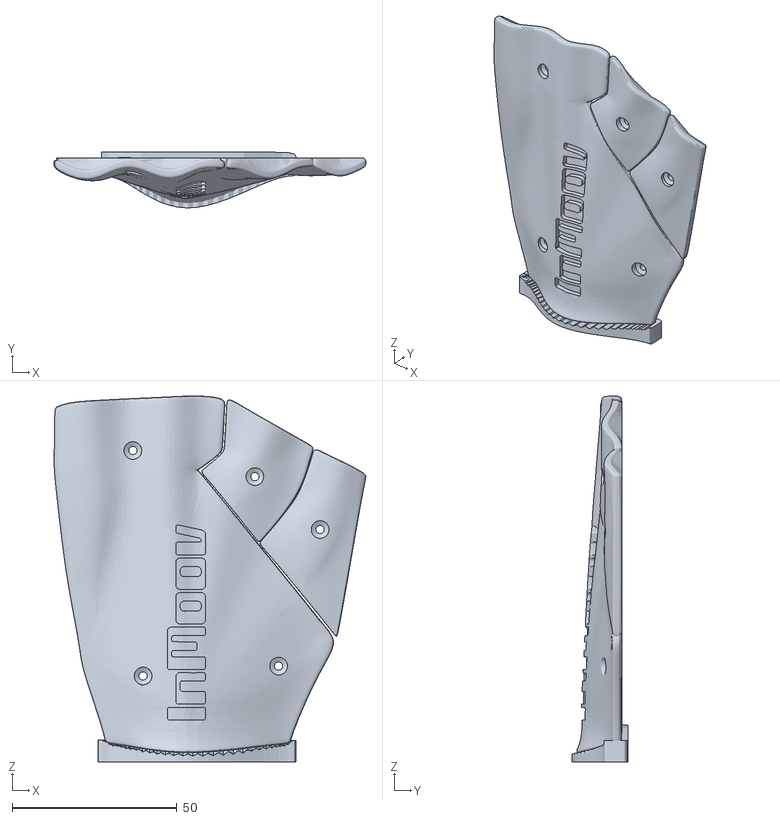
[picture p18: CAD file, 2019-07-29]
Hardware/Prosthetic/Right Hand/topsurfaceUP6.stl
94.7 x 17.0 x 111.2

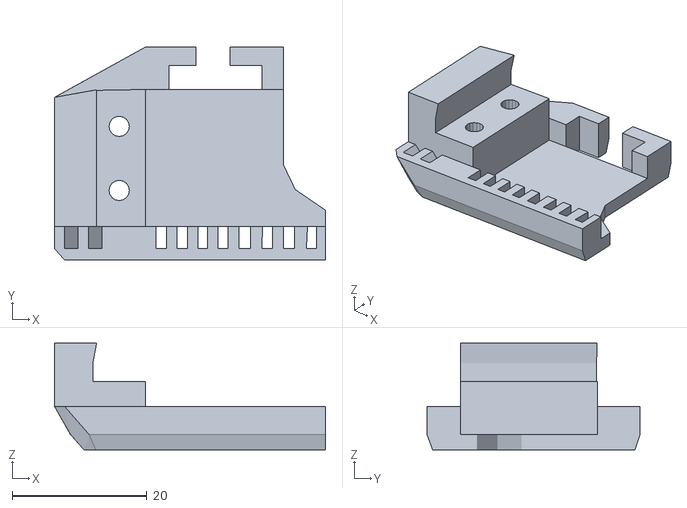
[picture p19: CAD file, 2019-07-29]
Hardware/Prosthetic/Right Wrist/CableHolderWristV5.stl
40.2 x 31.6 x 15.8

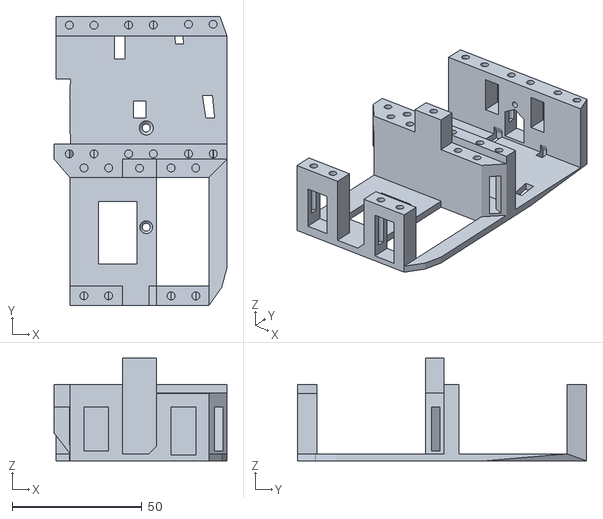
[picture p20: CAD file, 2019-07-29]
Hardware/Prosthetic/Right Forearm/RobServoBedV6.stl
66.7 x 111.6 x 39.7

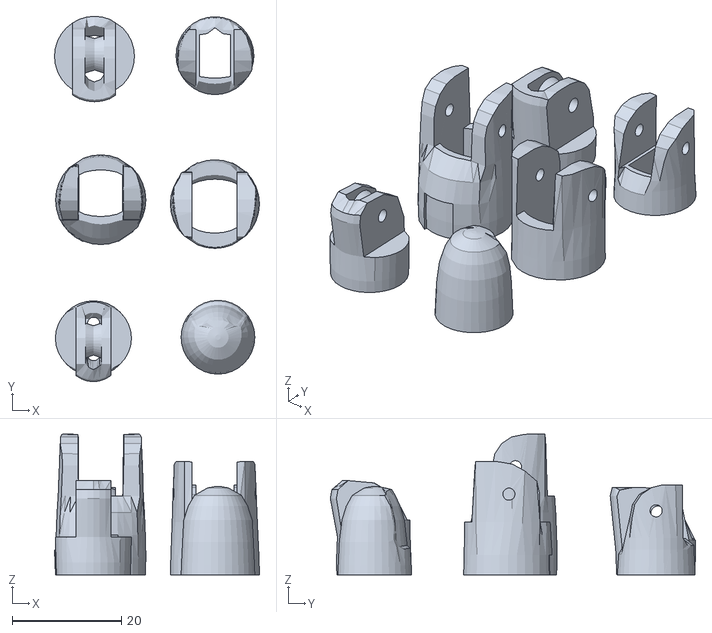
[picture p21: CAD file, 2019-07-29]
Hardware/Prosthetic/Right Hand/ringfinger3.stl
37.6 x 67.0 x 25.8

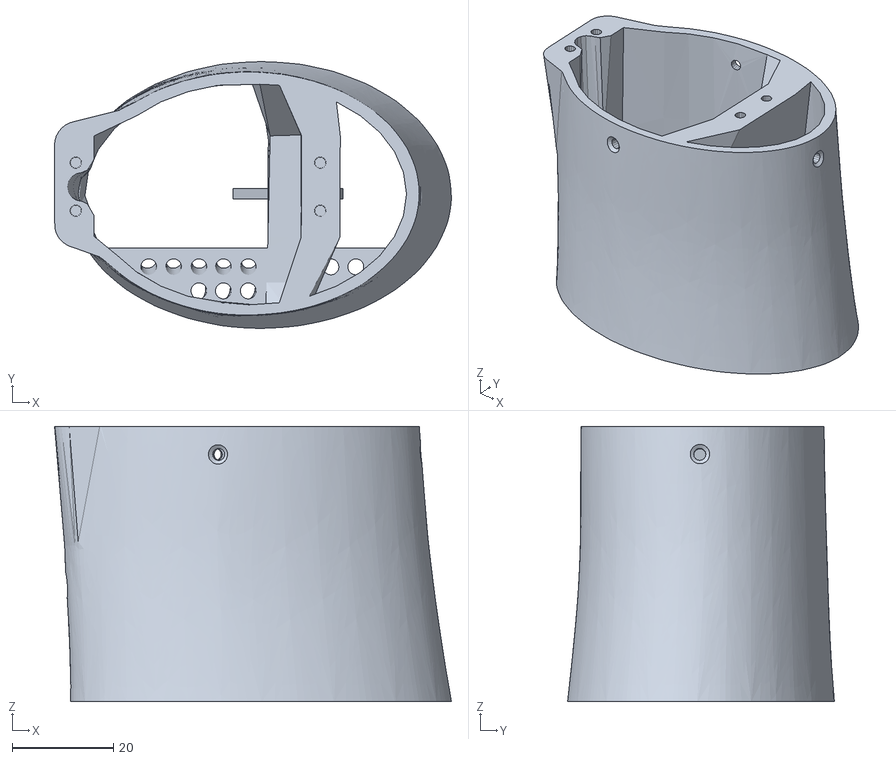
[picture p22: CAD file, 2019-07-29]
Hardware/Prosthetic/Right Wrist/RotaWrist1V4.stl
78.6 x 52.8 x 54.5

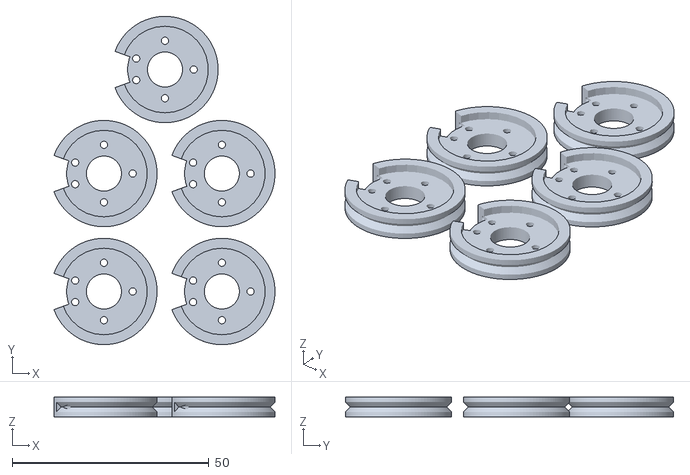
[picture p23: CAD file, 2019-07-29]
Hardware/Prosthetic/Right Forearm/servo-pulleyX5.stl
56.1 x 83.4 x 5.00

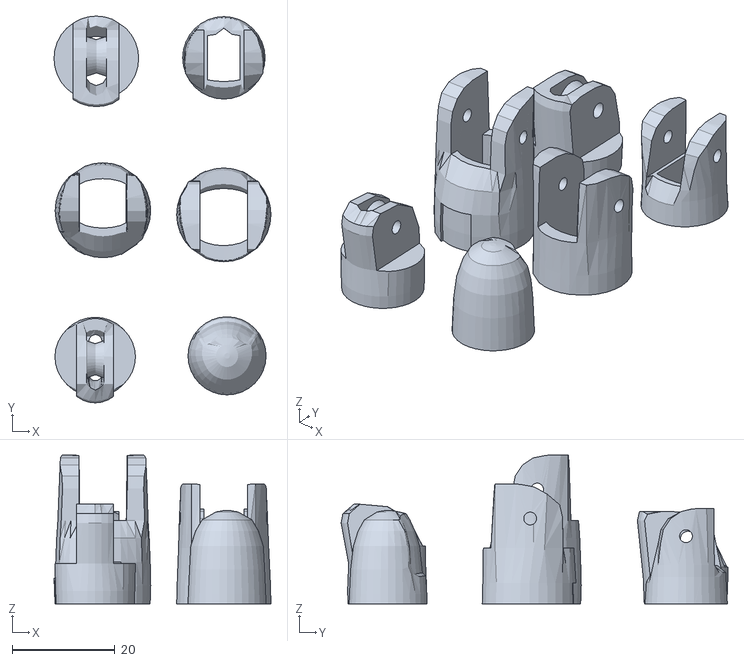
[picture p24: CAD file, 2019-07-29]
Hardware/Prosthetic/Right Hand/Majeure3.stl
42.2 x 75.2 x 29.0

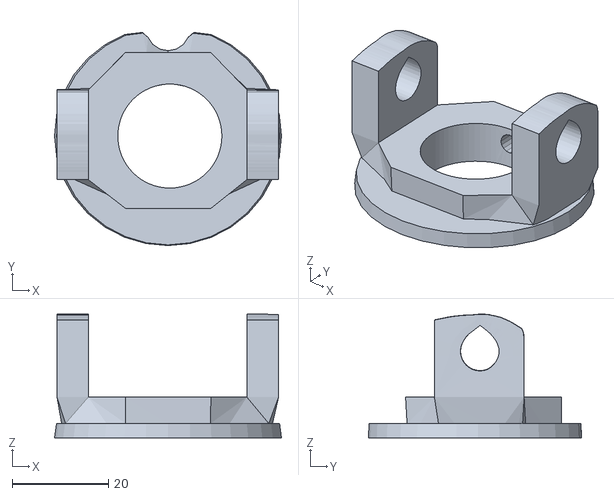
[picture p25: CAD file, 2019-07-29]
Hardware/Prosthetic/Right Wrist/RotaWrist3V3.stl
47.2 x 44.3 x 25.7

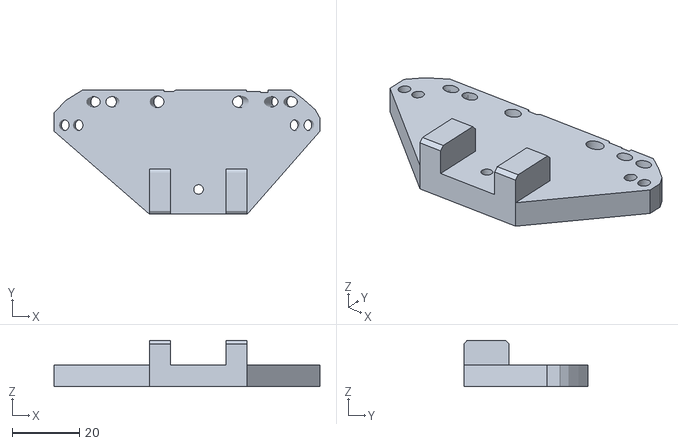
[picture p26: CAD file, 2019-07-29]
Hardware/Prosthetic/Right Forearm/RobCableFrontV3.stl
79.3 x 37.1 x 13.8

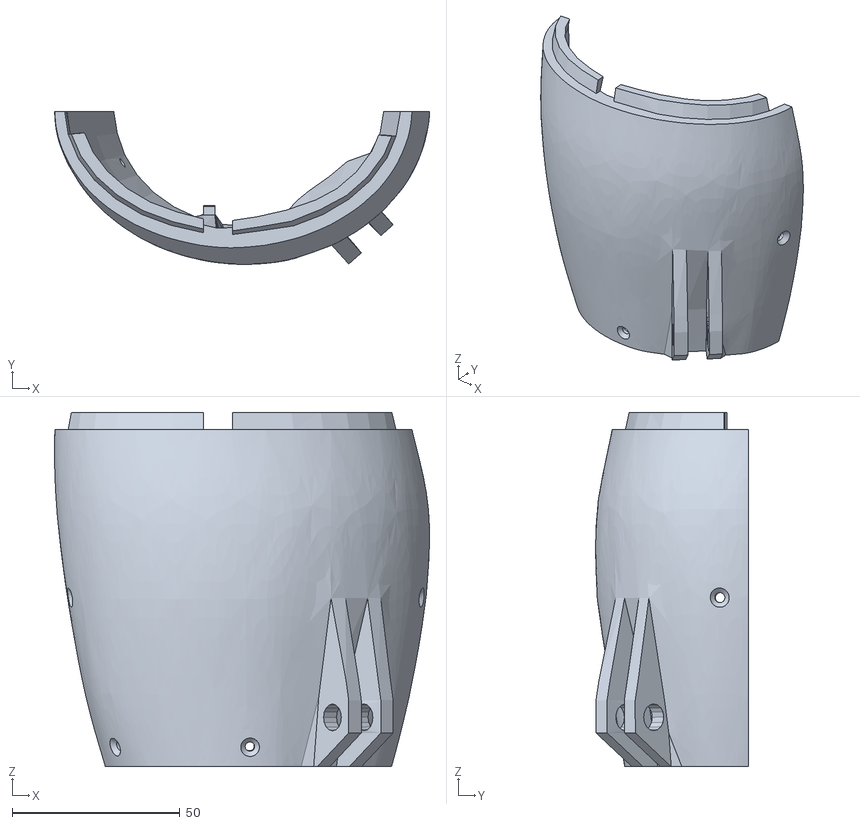
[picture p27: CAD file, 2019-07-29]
Hardware/Prosthetic/Right Hand/robpart4V4.stl
111.8 x 45.5 x 105.6

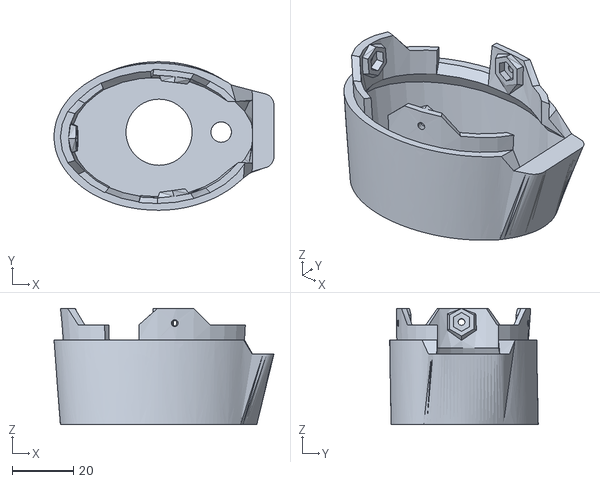
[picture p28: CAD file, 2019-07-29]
Hardware/Prosthetic/Right Wrist/RotaWrist2V3.stl
71.9 x 48.6 x 38.0

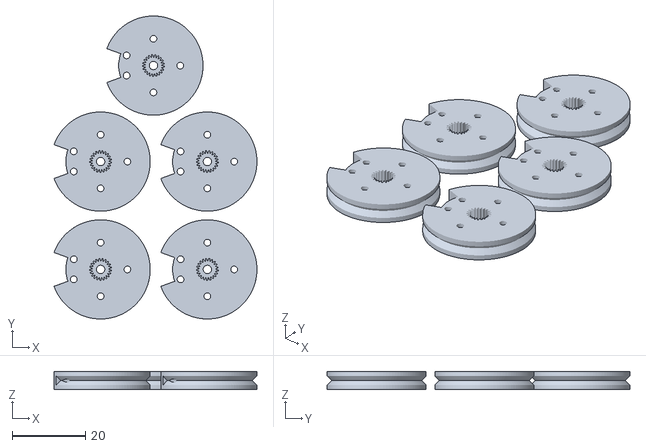
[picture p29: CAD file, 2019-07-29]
Hardware/Prosthetic/Right Forearm/RobRingV3.stl
55.3 x 82.5 x 5.00

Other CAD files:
Hardware/Prosthetic/Right Hand/coverfinger1.stl
Hardware/Prosthetic/Right Wrist/WristGearsV5.stl
Hardware/Prosthetic/Right Forearm/TensionerRightV1.stl
Hardware/Prosthetic/Right Hand/robpart5V4.stl
Hardware/Prosthetic/Right Hand/Auriculaire3 (pinky).stl
Hardware/Prosthetic/Right Hand/Bolt_entretoise7.stl
Hardware/Prosthetic/Right Hand/Index3.stl
Hardware/Prosthetic/Right Hand/WristlargeV4.stl
Hardware/Prosthetic/Right Hand/WristsmallV4.stl
Hardware/Prosthetic/Right Hand/robcap3V2.stl
Hardware/Prosthetic/Right Hand/robpart2V4.stl
Hardware/Prosthetic/Right Hand/robpart3V4.stl
Hardware/Prosthetic/Right Hand/thumb5.stl

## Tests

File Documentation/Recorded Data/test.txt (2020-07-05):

Device Configuration Complete! Waiting for operator...
Device Configuration Complete! Waiting for operator...
Starting data generation...
Let Hand Rest
Prepare to Close Hand...
3..
2...
1...
Start!

0	DE28E2
0	DCE1C6
0	DE48B5
0	DF19FC
0	DCF746
0	DD7228
0	DF8F99
0	DE960E
0	DD139C
0	DE4F62
0	DE2CC2
0	DCE4B8
0	DE53CA
0	DE32AD
0	DCFD7D
0	DEBAAF
0	DF8964
0	DD0AB5
0	DD1052
0	DF1DFE
0	DE2A8A
0	DD668A
0	DEB405
0	DE8C8B
0	DD0FF8
0	DE47D6
0	DE2DAC
0	DCE351
0	DE45B6
0	DF1B38
0	DCF794
0	DD63CC
0	DF7ACB
0	DE851F
0	DD0928
0	DF15A1
0	DE2545
0	DD0860
0	DE4124
0	DE25E4
0	DCDD5B
0	DE448C
0	DF15BA
0	DCDB1F
0	DD09C8
0	DF1B20
0	DCDC36
0	DD0AC1
0	DF1A74
0	DE2AE5
0	DD02BC
0	DE3C61
0	DE2652
0	DCEFAF
0	DEA9E7
0	DF7D95
0	DCFEEC
0	DE3914
0	DF1139
0	DCD8E4
0	DD0407
0	DF11E3
0	DE20F3
0	DD5A0C
0	DEA6F2
0	DE87BC
0	DD0012
0	DE311F
0	DE23B4
0	DCD52C
0	DE2B66
0	DF02B3
0	DCEB70
0	DD5940
0	DF7A3A
0	DE8C82
0	DCFDBB
0	DE3695
0	DE27B7
0	DCFA3B
0	DE2A80
0	DE1F08
0	DCD2CD
0	DE2D5E
0	DF06D5
0	DCE6D0
0	DD53AD
0	DF7D01
0	DE8BC2
0	DCF807
0	DF08EF
0	DE1E50
0	DCF149
0	DE2226
0	DE18D8
0	DCCF5F
0	DE2627
0	DF045E
0	DCCCCD
0	DCEFA0
0	DF0176
0	DCE41F
0	DD4EB9
0	DF7442
0	DE84EC
0	DCF42D
0	DE286E
0	DE20AF
0	DCCFD6
0	DE28E9
0	DF0235
0	DCE1C7
0	DE9018
0	DF690D
0	DCF577
0	DCECA9
0	DF00C7
0	DE1EE0
0	DD4736
0	DE8F99
0	DE89AB
0	DCF86F
0	DE227B
0	DE2229
0	DCCF43
0	DE196C
0	DEF980
0	DCE00A
0	DD41B0
0	DF6774
0	DE7F9F
0	DCEAE9
0	DE1B67
0	DE1BE2
0	DCEDA2
0	DE2178
0	DE2168
0	DCC97A
0	DE138E
0	DEF447
0	DCDDE8
0	DD3CBD
0	DF6318
0	DE7DAC
0	DCE659
0	DEFFFD
0	DE2125
0	DCE9BD
0	DE1CE5
0	DE235C
0	DCC529
0	DE1182
0	DEF328
0	DCC3D6
0	DCE225
0	DEF68A
0	DCD9AA
0	DD3669
0	DF635A
0	DE7F8D
0	DCD9F7
0	DE08A5
0	DE1551
0	DCBF00
0	DE0293
0	DEE64D
0	DCD4C1
0	DE7D73
0	DF6601
0	DCF2A9
0	DCD60C
0	DEF212
0	DE1BA5
0	DCDC69
0	DE0C46
0	DE1F3E
0	DCC348
0	DE0884
0	DE1D44
0	DCD78B
0	DE751F
0	DF5BAE
0	DCEE63
0	DCD213
0	DEEA2A
0	DE18CB
0	DCCF16
0	DDFF7C
0	DE15F9
0	DD2B47
0	DE6DF4
0	DE8359
0	DCED43
0	DDF612
0	DEDF70
0	DCBC43
0	DCD1E8
0	DEEE18
0	DE1F98
0	DD221E
0	DF5B6C
0	DE8696
0	DCCB75
0	DDF2DF
0	DE1971
0	DCBD91
0	DDF994
0	DEE55C
0	DCB8AD
0	DCC3A4
0	DEDE60
0	DCCD1B
0	DD2039
0	DF5CAC
0	DE899C
0	DCC839
0	DDF4AA
0	DE1C73
0	DCBC19
0	DDF459
0	DEE4B3
0	DCBF09
0	DCC43B
0	DED82B
0	DCC810
0	DD181C
0	DF4CAF
0	DE7C47
0	DCC066
0	DDE760
0	DE117E
0	DCCABC
0	DE5BC0
0	DF4F81
0	DCF12B
0	DDE1C9
0	DED4A0
0	DCB161
0	DCBAB5
0	DED88D
0	DE11E1
0	DCB9B8
0	DDE359
0	DE139A
0	DCB60D
0	DDE524
0	DE1DA9
0	DCCAB7
0	DE4873
0	DF3BB9
0	DCE0DD
0	DCBAC4
0	DEE012
0	DE198B
0	DCBE8F
0	C00000
0	DE1CE9
0	DCBA31
0	DDE4DC
0	DE1BA6
0	DCC9C9
0	DE49BB
0	DF4162
0	DCE76E
0	DCB4D7
0	DED93F
0	DCB2EA
0	DCB702
0	DEDAE4
0	DE1DC4
0	DD0577
0	DE46D4
0	DE857D
0	DCE7BD
0	DDD512
0	DED08E
0	DCB23C
0	DDD9D0
0	DED59E
0	DCB003
0	DCADFE
0	DED4DF
0	DE1B5F
0	DD034C
0	DE439D
0	DE8507
0	DCE85D
0	DDC600
0	DE0EB0
0	DCAE43
0	DDC6D5
0	DEC387
0	DCBE74
0	DCFDB8
0	DF3DDB
0	DE83BE
0	DCA974
0	DDC980
0	DE1752
0	DCAABB
0	DDCA86
0	DE1E25
0	DCB1B6
0	DDC66E
0	DECA30
0	DCAD3A
0	DCA142
0	DEC646
0	DE175E
0	DCF696
0	DF3891
0	DE84AB
0	DCA543
0	DDC1AD
0	DE1660
0	DCA95C
0	DDBB6B
0	DEC225
0	DCBC2E
0	DCF5E3
0	DF3A66
0	DE8D89
0	DCA241
0	DEC308

Stop! Let Hand Rest...

Prepare to Open Hand...
3..
2...
1...
Start!

1	DC0FA7
1	DCFB4C
1	DE0C0E
1	DC807A
1	DCF492
1	DE3BE7
1	DC82B4
1	DC4544
1	DEA935
1	DE7672
1	DC0CAD
1	DCF6FF
1	DE0F03
1	DBFF29
1	DCEBC3
1	DE0545
1	DC84F7
1	DD5D5F
1	DEA822
1	DCC96A
1	DC079D
1	DE3775
1	DE0855
1	DC0606
1	DE40A0
1	DE1146
1	DC019E
1	DCF1C9
1	DE1274
1	DC804A
1	DCF1BE
1	DE3DAB
1	DC8296
1	DC1C53
1	DCD8C8
1	D11A3E
1	C7E263
1	C797BB
1	C79BEB
1	C79ABF
1	C79A9A
1	C7A25E
1	C7A341
1	C7A214
1	C7A598
1	C7AA5F
1	C7A925
1	C7AD55
1	C7B22F
1	C7B11A
1	C7B568
1	C7B938
1	C7B944
1	C7B9FF
1	C7C15F
1	C7C26A
1	C7C21D
1	C7C5BD
1	C7CA89
1	C7C9A8
1	C7CDD3
1	C7D264
1	C7D161
1	C7D59A
1	C7D94C
1	C7D942
1	C7D9F6
1	C7E135
1	C7E23F
1	C7E1B9
1	C7E526
1	C7E9C3
1	C7E8C7
1	C7ECD0
1	C7F16E
1	C7F081
1	C7F483
1	C7F82E
1	C7F848
1	C7F8C3
1	C7FFFD
1	C80138
1	C8008A
1	C80302
1	C80147
1	18
1	C7FDCD
1	C7FC10
1	C7F818
1	C7F6F0
1	C7F44D
1	C7F251
1	C7EF71
1	C7ECE1
1	C7EAE9
1	C7E806
1	C7E710
1	C7E381
1	C7E1BB
1	C7DF97
1	C7DE0E
1	C7DA3B
1	C7D911
1	C7D69A
1	C7D2C6
1	C7D192
1	C7CF13
1	C7CD17
1	C7CA21
1	C7C918
1	C7C58D
1	C7C3C4
1	C7C1BC
1	C7C025
1	C80746
1	CF3686
1	D38394
1	DA8A13
1	DCBA6C
1	DF02CD
1	DFC4A1
1	E2ADD8
1	E4501B
1	E72527
1	E8E8EC
1	ECA628
1	EF4EB4
1	F0A965
1	F31212
1	F40D78
1	F5F31D
1	F7098E
1	F8C4FD
1	F95E9D
1	FAB59C
1	FB638E
1	FC6665
1	FD8768
1	FE1FB2
1	FF9694
1	CD4C
1	40A98
1	5C0EA
1	74C75
1	9ECCB
1	AF2E1
1	C2FDB
1	CA6BF
1	D8BA2
1	DD606
1	E4B47
1	EA204
1	F100C
1	F0B68
1	F01D2
1	EFB34
1	ECB06
1	E491A
1	E2A50
1	DD06E
1	D8639
1	D3A4A
1	D2E84
1	CE18D
1	CC770
1	CCE0D
1	CB2F4
1	C72E1
1	C8A2E
1	CE21A
1	D595B
1	105CD5
1	136F1A
1	133E03
1	11B1BE
1	11DFC9
1	11E0FD
1	11DF3D
1	11DD6C
1	11DC02
1	11D859
1	11D67F
1	11D52C
1	11D1AF
1	11D0B2
1	11CEAA
1	11CCEE
1	11CA48
1	11C987
1	11C694
1	23
1	11C341
1	11C21E
1	11BEDD
1	11BD46
1	11BC14
1	11B8CA
1	11B7E0
1	11B627
1	11B475
1	11B1FE
1	11B161
1	11AEB3
1	11AC4
1	11ABBB
1	11A94F
1	11A7F7
1	11A6E9
1	11A627
1	11A391
1	11A319
1	11A26C
1	11A146
1	11A015
1	119
1	119F15
1	119E7B
1	119F23
1	11A065
1	11A1F6
1	11A997
1	11AE37
1	11C0C8
1	11DACC
1	1141A1
1	114D53
1	107F30
1	F9FFB
1	AC12F
1	814B7
1	4AB4F
1	32026
1	162CD
1	BD81
1	FC5FD3
1	FA4221
1	FAA801
1	C00000
1	F99E41
1	F6E960
1	F60AB3
1	F4D346
1	F46E4B
1	F3E8A8
1	F38A44
1	F2B5FB
1	3C911
1	F205AC
1	F1BAC8
1	F13CDA
1	F0D00B
1	F091B5
1	F04A90
1	F04033
1	F030FF
1	F05019
1	F0F285
1	F1422D
1	F1D15A
1	F235FB
1	F2E9B8
1	F326AE
1	F3DAD5
1	F49B2E
1	F4D809
1	F57063
1	F5BF34
1	F62E15
1	F67060
1	F71E0E
1	F75F26
1	F7D9F0
1	F8C8D4
1	F936E8
1	F9ED1C
1	FA625E
1	FB3C02
1	FB8F0A
1	FC9AC4
1	FD8960
1	FF82E3
1	8387
1	29BF2
1	38646
1	57763
1	6B43E
1	8E5B5
1	97139
1	A8720
1	B63A9
1	CE175
1	D1B8F
1	D38FC
1	D3C17
1	D3825
1	D371F
1	D3509
1	D332A
1	D3049
1	D2F79
1	D2C68
1	D2AB4
1	D28E9
1	D27C1
1	D245C
1	D2347
1	D2178
1	D1FC1
1	D1D11
1	D1C69
1	D19A0
1	D1802
1	D165B
1	D154A
1	D1208
1	D110A
1	D0F50
1	D0DB6
1	D0B3F
1	D0AA5
1	D080E
1	D0686
1	D0512
1	D041C
1	D0107
1	D0023
1	CFEC2
1	CFD78

Stop! Let Hand Rest...

Prepare to Close Hand...
3..
2...
1...
Start!

0	E529E
0	ED736
0	1288FE
0	118AAE
0	E49CC
0	127C11
0	141EFC
0	E4175
0	EBDA8
0	140E4E
0	117159
0	E9BBE
0	1250FF
0	11731F
0	E2D4A
0	1244C9
0	13FB36
0	E2732
0	E8C97
0	1237A9
0	11664D
0	E7BB3
0	122A17
0	13E759
0	E103F
0	E696E
0	13DAAE
0	1157CC
0	E599E
0	1205C1
0	115024
0	E04B5
0	11F2C5
0	13C2FB
0	DF782
0	E3E0F
0	13C3CA
0	114FD5
0	E3946
0	11DCAB
0	11449E
0	DECEE
0	11C9D5
0	13B240
0	DEAC7
0	E1ADB
0	11B2C9
0	114539
0	DE96E
0	11AC59
0	13981C
0	DE529
0	E0919
0	139853
0	113BB1
0	DF18E
0	1186DF
0	113288
0	DCFB8
0	1173AE
0	13745B
0	DC47D
0	DD4A6
0	1369BE
0	111E32
0	DC3F6
0	1156DD
0	111BA9
0	DADCC
0	11437A
0	13576B
0	DAA85
0	DAA87
0	1137A4
0	1112B6
0	1B36C
0	1127F6
0	133D32
0	D9903
0	D8C79
0	133A75
0	110515
0	D7FA1
0	110804
0	11002F
0	D8807
0	10F089
0	131BE5
0	D7C7E
0	D5D80
0	1319F2
0	10F6BE
0	D5224
0	10D708
0	10F6C0
0	D8087
0	10CADC
0	130250
0	D6B33
0	D3A02
0	10B9A2
0	10E37D
0	D286B
0	10A2CE
0	12E98F
0	D5931
0	D14E8
0	12E05B
0	10D627
0	D12BB
0	10894C
0	10D0AE
0	D5501
0	10766A
0	12CAB1
0	D480D
0	CF58A
0	12BD56
0	10C716
0	CE3AE
0	105206
0	10B338
0	D320C
0	103D5C
0	12A039
0	D29F5
0	CC4EE
0	102C76
0	10AFED
0	D1FB9
0	101A3B
0	1282FA
0	D1813
0	CA572
0	127688
0	1098AC
0	C96B7
0	FF3C4
0	1094FF
0	D04E4
0	3F
0	125A5D
0	1086F0
0	C7AEE
0	FD595
0	108CE8
0	CF7D6
0	C63AA
0	124515
0	107B68
0	C59A0
0	FB31E
0	107D9E
0	CE82F
0	FA36C
0	1231CD
0	CE4E7
0	C4318
0	F8C15
0	106F64
0	CD5C3
0	F75BC
0	1215C1
0	CD1AA
0	C239A
0	F6D88
0	10683F
0	CD10F
0	F58FD
0	11FBCB
0	CC791
0	C0BDC
0	F49A0
0	105E77
0	CBE3D
0	F3A6D
0	11F150
0	CB24E
0	BE943
0	F2428
0	104B35
0	CA5DB
0	F140D
0	11CE99
0	CAA39
0	BD5EF
0	11C9F9
0	10468F
0	BBFA3
0	EEE9F
0	11AC27
0	C8B7F
0	BA90D
0	11AB09
0	10304A
0	BA8A4
0	ED3DC
0	1032C2
0	C9382
0	EC13B
0	119650
0	C00000
0	B8A33
0	EB30C
0	102859
0	C7E24
0	E9EE7
0	117965
0	C7533
0	B7398
0	E8E8A
0	101AD8
0	C77AF
0	E7F2F
0	116103
0	C67D0
0	B5802
0	E66CF
0	100494
0	C55A0
0	E5268
0	1137C7
0	C4C2F
0	B3230
0	E4119
0	FED34
0	C488A
0	E3146
0	1126FD
0	C4F71
0	B22F1
0	E1F3F
0	FF22F
0	C4C7D
0	E13A0
0	110CEB
0	FE43C
0	B0186
0	DF747
0	FDAAA
0	C37C2
0	AF87B
0	10EA37
0	FD490
0	AE19E
0	DCCBB
0	FCD04
0	C269E
0	AD9EA
0	10D491
0	FC82D
0	ACC36
0	DB720
0	FC231
0	C1BE9
0	AC2DE
0	10BC26
0	FC077
0	AB36C
0	D91FF
0	109D2B
0	C0DA9
0	AAFD9
0	1097A4
0	FB1E5
0	A9F7A
0	D6AFD
0	FA1F2
0	C02CF
0	A8D5D
0	108258
0	FA4FE
0	A8064
0	D4A37
0	106E0A
0	BF76E
0	A77E1
0	105E1D
0	F93CA
0	A6A35
0	D25C9
0	10518E
0	BE3C2
0	A5B32
0	103742
0	F76DB
0	A43A1
0	CFA28
0	101EB4
0	BC83E
0	A3251
0	1018CB
0	F632B
0	A285B
0	CD3B1
0	F5EBB
0	BC0F5
0	A20A9
0	FFEF4
0	F5D79
0	A10B2
0	CB626
0	FEE8B
0	BAFB3
0	A0676
0	FDEEF
0	F49AE
0	BAADF
0	C966B
0	FD7CE
0	BAC67
0	9EE6A
0	C7E91
0	F3BC0
0	B9BE6
0	C00000
0	FB4B3
0	F2EBE
0	9D4FF
0	C576B
0	F1EC2
0	B8C46
0	9C1E9
0	F932F
0	F1E1C
0	B88E0
0	C38F8
0	F893D
0	B80C0
0	9A96F
0	C1BF5
0	F0D3A
0	B76AD
0	C0C37
0	F6340
0	B6B85
0	98ED0
0	BF6E2
0	F0201
0	B7080
0	BEB78
0	F446E
0	EF27A
0	97A0F
0	BDC98
0	F3632

Stop! Let Hand Rest...

Prepare to Open Hand...
3..
2...
1...
Start!

1	57C4F
1	7B1B6
1	B1FD9
1	7A472
1	58A8D
1	7BA71
1	B3F2F
1	7BC3D
1	5901B
1	B38FC
1	B4F7A
1	5A752
1	7C9E6
1	B4258
1	7EF93
1	5BFF8
1	7D6C1
1	B7DD0
1	806FF
1	FB
1	B678D
1	B9B01
1	82241
1	7E78B
1	B6DA8
1	8354E
1	5E983
1	7ED4E
1	BB45A
1	84548
1	5F496
1	B7CD8
1	BCCC7
1	60CE1
1	80170
1	B85E6
1	8740B
1	6196F
1	803C5
1	BEF6D
1	88C15
1	81299
1	B9C1F
1	C0083
1	633BA
1	81407
1	B9997
1	8B521
1	65038
1	2EBC
1	C2C2E
1	8CF3D
1	8216E
1	BB4A9
1	C2E3C
1	662D1
1	826E5
1	BBE70
1	8F3E4
1	672CD
1	BC958
1	C5E99
1	90B76
1	83744
1	BD4B4
1	92976
1	6932D
1	83D93
1	C7D9A
1	93C18
1	69FB3
1	BE15A
1	C8FD1
1	95274
1	850A2
1	BEAC7
1	967C9
1	6C5B5
1	856FE
1	CB076
1	97BF6
1	6D8DF
1	C0436
1	CD094
1	6F9A3
1	87736
1	C07AD
1	9B571
1	6FA09
1	86B76
1	CF11A
1	9C983
1	873FF
1	C13F3
1	CEDC6
1	71457
1	87637
1	C1AB2
1	9F440
1	72D4B
1	C2DF7
1	D1F2A
1	A07D4
1	88B45
1	C3701
1	D33B5
1	750CA
1	89FB5
1	C00000
1	A35BE
1	756CF
1	C41E2
1	D4E12
1	A44CE
1	8A29A
1	C4978
1	A60DD
1	77ABE
1	8A6D1
1	D7615
1	A7577
1	78B6B
1	C688A
1	D8FDB
1	F399
1	8C171
1	C6873
1	AA47F
1	7AE3C
1	8C616
1	DAAEA
1	AB701
1	C00000
1	C7645
1	DB057
1	7CFB4
1	8D97F
1	C8587
1	AE486
1	7DD45
1	C8809
1	DD811
1	AF91F
1	8E2B3
1	C982D
1	DEBB6
1	805AD
1	8EDE7
1	DFB9B
1	B256C
1	80E7B
1	CAA15
1	E1021
1	B3B17
1	90518
1	CB567
1	B54A5
1	83419
1	90752
1	E34CB
1	B6DEE
1	84755
1	CBB97
1	E39AF
1	850D3
1	91158
1	CBB8F
1	B9290
1	86D31
1	92053
1	E5FB3
1	BAB6B
1	8C000
1	CD917
1	E68B9
1	88E51
1	933EC
1	CDDCC
1	BD5DB
1	89C43
1	C00000
1	E8A16
1	BE616
1	942DD
1	CEF46
1	E935C
1	8C040
1	943E4
1	EA749
1	C1464
1	8D2CA
1	CFBF9
1	EC104
1	C2EE9
1	9643B
1	D0678
1	C45D2
1	8F5FB
1	95AA8
1	ECB02
1	C4A7A
1	8FC41
1	D0350
1	EDC69
1	90CF3
1	96959
1	D0902
1	C7A34
1	91FE7
1	967FC
1	EFB1D
1	C9749
1	93A0C
1	D1B3D
1	F055E
1	95935
1	99391
1	D256D
1	CC55E
1	95E6F
1	98777
1	F1A9C
1	CC810
1	99340
1	D2671
1	F2F6B
1	97DC4
1	9984E
1	D27AC
1	CF8D1
1	990EE
1	D2FF3
1	F4965
1	D093D
1	9A6AF
1	D3727
1	F5CD7
1	9B213
1	9B3D1
1	F6DB2
1	D45B0
1	9CD7A
1	D4728
1	F7E39
1	D5852
1	9D152
1	D56FB
1	D6DFB
1	9F5B9
1	9D58D
1	F9808
1	D8224
1	9FA39
1	D512F
1	F952A
1	C00000
1	9D202
1	D495A
1	D992D
1	A16D7
1	9D376
1	FB7F8
1	DBA2D
1	9EB2D
1	D5D57
1	FB2DD
1	A48B4
1	9F5AB
1	D5FDF
1	DE08E
1	A5CD8
1	D6200
1	FD38E
1	DF461
1	A08F2
1	D6E62
1	FE5BB
1	A8C82
1	A1BB8
1	C00000
1	E260B
1	A96D5
1	D783D
1	1000EC
1	AB4C1
1	A2F94
1	D845E
1	E54B3
1	AC5F0
1	A2C49
1	1017F7
1	E5E21
1	A3455
1	D87EC
1	E6EC0
1	ADF53
1	A3CD4
1	102FB8
1	E8C11
1	A4DBE
1	D9444
1	103743
1	B114A
1	A56C7
1	104B4D
1	EB9E8
1	B1B3D
1	D9BC9
1	1051F6
1	B2C31
1	A5F0E
1	D9A38
1	EDE03
1	B3FB8
1	D9B8F
1	1061B9
1	EE85E
1	A750B
1	DA178
1	F090F
1	B6E32
1	A82AF
1	10838F
1	F1A00
1	A8920
1	DB015
1	10831C
1	B8E49
1	A9C02
1	109608
1	F3C0A
1	A9E6F
1	DB65B
1	109AAB
1	BAFBB
1	AAA3A
1	10A405
1	F6120
1	BC3F4
1	DC1AF
1	10A712
1	BD02A
1	AB5D4
1	DC070
1	F8990
1	BE7AC
1	DC316
1	10C047
1	F9860
1	AC581
1	DC5D0
1	FB677
1	C1495
1	AD22C
1	10D997
1	FC528
1	ADFE5
1	DD5DC
1	10E845
1	C3C34
1	AF76D
1	10F656
1	FF8B8

Stop! Let Hand Rest...

Prepare to Close Hand...
3..
2...
1...
Start!

0	1348D9
0	16E3AC
0	137138
0	113192
0	16EBCE
0	16EFBD
0	113DA2
0	134B3D
0	16F48B
0	13982B
0	13474E
0	16EEF4
0	13A85C
0	134F51
0	16F6C3
0	13BCB2
0	1167FE
0	16FFE2
0	172588
0	11755A
0	135953
0	172A66
0	13E974
0	13623E
0	173BDD
0	13FCCB
0	136529
0	1703DA
0	140C7B
0	11A49B
0	170005
0	174AF9
0	11B3A5
0	13629B
0	175613
0	11CA48
0	136F88
0	175905
0	144924
0	13729F
0	170166
0	14641E
0	11FF2C
0	170016
0	176B45
0	121C11
0	16F739
0	177653
0	124020
0	139EC6
0	1777FB
0	14BAC6
0	13A895
0	16F5FF
0	14DB2E
0	1293ED
0	16F150
0	14F14C
0	12AF00
0	16E962
0	178B9D
0	12DA07
0	13E670
0	178571
0	152E91
0	1402A2
0	16E984
0	155486
0	143C85
0	16FBE0
0	156D47
0	138CB6
0	17071C
0	178B40
0	13A80B
0	14807B
0	17933D
0	1597EE
0	1494CE
0	17A06A
0	15A0C3
0	1496DB
0	17231F
0	15B44F
0	13DA47
0	172B60
0	17B570
0	13EC2C
0	14B564
0	17B4C1
0	140FB7
0	14D263
0	17B744
0	15DB88
0	14E03C
0	1744E3
0	15E801
0	1431AA
0	1746A1
0	17C3E4
0	1437EE
0	174B9A
0	17D711
0	14482B
0	14F2FB
0	17E7EF
0	161B38
0	14ECFB
0	174D41
0	16216F
0	1453AD
0	1743FB
0	163393
0	1469EA
0	174B0F
0	17FB04
0	147BD4
0	150145
0	180A7E
0	165B0D
0	15073A
0	1756CE
0	166DBC
0	152D3C
0	175D1B
0	168020
0	14EA12
0	17706B
0	18053E
0	1521F2
0	159A8F
0	1809BF
0	16AA1C
0	15B4E6
0	18113F
0	16B993
0	15C369
0	179C84
0	16C212
0	156F98
0	17A810
0	181B5B
0	1581EE
0	15ED17
0	1823B5
0	159971
0	16031B
0	1829E9
0	16E658
0	160ADE
0	17C805
0	16F48E
0	15BC04
0	17D746
0	183790
0	15BFDC
0	17D9B3
0	183C83
0	15D057
0	1634F5
0	184B84
0	171A7C
0	16415B
0	17EEE8
0	1717D5
0	15DB2C
0	17EA0F
0	17239C
0	15E856
0	17F29F
0	186080
0	15F6D1
0	16516A
0	186B2D
0	173D48
0	1659FD
0	1802DC
0	174391
0	160DFD
0	1808A8
0	1879BF
0	161FC1
0	1812D0
0	1881FF
0	162934
0	167A57
0	188638
0	1765D7
0	167E4F
0	181B6E
0	177599
0	1649EC
0	182687
0	178292
0	1658BE
0	182A37
0	189B05
0	165C63
0	169BA0
0	18A7AC
0	1795B3
0	16A50A
0	1834FD
0	179922
0	166BC0
0	1837D6
0	17AB6F
0	167E74
0	1840F5
0	18BF2C
0	1682CA
0	16B8AF
0	18CF00
0	17C41F
0	16C17D
0	1850BD
0	17C8EC
0	5AF
0	1850B9
0	18DE57
0	169A19
0	16BF9E
0	18F2DE
0	17E78D
0	16C161
0	18F7E2
0	17F2DB
0	16C5E9
0	18535E
0	17FAB7
0	16BD5F
0	1858BB
0	1901E3
0	16C496
0	16CFAA
0	190F31
0	16CE68
0	16C2DC
0	18E812
0	17F562
0	16E7DA
0	1878FE
0	183426
0	16FA9A
0	189FA8
0	195286
0	170A76
0	18AE1F
0	1955D6
0	17084A
0	171773
0	195615
0	184F7A
0	171602
0	18A4BD
0	185291
0	1713FA
0	18A3BF
0	185144
0	1718C2
0	18AB83
0	19586C
0	172332
0	172FAB
0	196227
0	186F47
0	174155
0	18C6BA
0	187665
0	1744
0	18BF57
0	196D8B
0	174E87
0	380000
0	197F18
0	175E13
0	175E2C
0	19822F
0	189750
0	175D50
0	18D11F
0	189DCD
0	176D48
0	18D681
0	198C71
0	176F4B
0	18D6AF
0	1991FD
0	177AF4
0	176CA3
0	199604
0	18B53A
0	1775E5
0	18E2A8
0	18BF08
0	178EBB
0	18E43E
0	18C228
0	17945C
0	18E931
0	19AB2C
0	179FDB
0	178B29
0	19B2DF
0	18DDC2
0	17940F
0	18F8FD
0	18E6DA
0	17984C
0	18FB7D
0	18F356
0	17C4D4
0	19071A
0	19D33E
0	17D6CF
0	17B429
0	19D731
0	1902A5
0	17B01B
0	19D668
0	190E7E
0	17BB1C
0	191426
0	191504

Stop! Let Hand Rest...

Prepare to Open Hand...
3..
2...
1...
Start!

1	19E007
1	19D4F4
1	19D0BC
1	19D979
1	19D320
1	19CE98
1	19D783
1	19DC61
1	19CCBE
1	19CCF8
1	19DA76
1	700000
1	19CB27
1	19D864
1	19CD27
1	19C912
1	19D0F3
1	19CAD7
1	19C71F
1	19CF85
1	19D39D
1	19C4B5
1	19C4E4
1	194EFF
1	17D080
1	18C6D1
1	1904D9
1	18D23F
1	18A9DF
1	18CAC4
1	190BBC
1	191BB3
1	19635E
1	19486E
1	18D83C
1	189
1	1834B0
1	17C89E
1	179642
1	17BEA3
1	17CA0F
1	179121
1	16855A
1	149B26
1	138958
1	119F47
1	10866A
1	E60DA
1	D88E7
1	BF34D
1	B2B13
1	A7B3E
1	94F13
1	8A9D9
1	75831
1	711FF
1	66FEF
1	634DC
1	6F101
1	746C5
1	7610C
1	7583B
1	7860E
1	7E678
1	7EF94
1	83978
1	8728D
1	858FF
1	840D3
1	851FD
1	80BEC
1	7707C
1	6DC13
1	6E88D
1	6EEFF
1	6ED13
1	6EAD5
1	6E96C
1	6E596
1	6E455
1	6E20C
1	6E02D
1	6DD24
1	6DC48
1	6D93D
1	6D772
1	6D55A
1	6D41D
1	6D0A4
1	6CF6C
1	6CD73
1	6CBAC
1	6C8C6
1	6C7FE
1	6C51C
1	6C364
1	6C179
1	6C05F
1	6BEB4
1	6BBE0
1	6BB26
1	6B863
1	6B6AB
1	6B6D0
1	6AED2
1	47C69
1	214A7
1	FD7A0E
1	FB707F
1	F81B1C
1	F6D185
1	F4505D
1	F34E4C
1	F2402C
1	F143DB
1	F0E069
1	F09D49
1	F0563D
1	EF5DC3
1	EEFE62
1	EE0F95
1	ED3FF4
1	EC7999
1	EC5475
1	EBCF7D
1	EB908A
1	EB6A3B
1	EB0ADD
1	EAF3A1
1	EB3083
1	EB45DA
1	EB566F
1	EB8ABF
1	EBECE9
1	EBF4BA
1	EC24AE
1	EC6727
1	EC5E99
1	EC8A54
1	ECC0F6
1	ECEEE1
1	ED0561
1	EDCF2E
1	EE71EE
1	EFD54F
1	F0BE7A
1	F28B00
1	F3BA39
1	F44A61
1	F50B23
1	F52611
1	F55CA4
1	F57CE5
1	F560A8
1	F54BAB
1	F556C1
1	F544C5
1	F4FBAE
1	F501C6
1	F4E423
1	F38ED6
1	F2FAC6
1	F1F159
1	F151DB
1	F053B1
1	EFE900
1	EEB5A1
1	EDF428
1	ED4152
1	ECF4C0
1	EB9605
1	EB53E1
1	EB0F24
1	E951EE
1	E90E04
1	E9085F
1	E90646
1	E902F0
1	E901E9
1	E8FEBE
1	E8FCD9
1	E8FA9D
1	E8F7A0
1	E8F5BC
1	E8F386
1	E8F260
1	E8EECE
1	E8ED81
1	E8EB7B
1	E8E9C0
1	E8E6AD
1	E8E4B0
1	E8E2F2
1	E8DFC7
1	E8DEF5
1	E8DC1B
1	E8DA34
1	E8D824
1	E8D70D
1	E8D383
1	E8D241
1	E8D066
1	E8CCE0
1	E8CBAA
1	E8C9D5
1	E8C827
1	E8C544
1	E8C483
1	E8C1F8
1	E8C032
1	E8BE66
1	E8848F
1	E6D60F
1	E3D9A6
1	E25B78
1	E02C1D
1	DF7B53
1	DE6F68
1	DDFB36
1	DDC783
1	DDDC56
1	DDD8F2
1	DDC63C
1	DE130B
1	DE69C7
1	DEEC18
1	DFDB6D
1	E055CE
1	E11B25
1	E1891A
1	E26C85
1	E2BB5D
1	E3513D
1	E3A0A8
1	E40623
1	E438E4
1	E4E3FB
1	E58962
1	E5D3D2
1	E685A5
1	E6C551
1	E7080D
1	E74163
1	E7BE3A
1	E7E4C5
1	E84BFE
1	E897E8
1	E8F3B5
1	E93E03
1	E9700F
1	E9BA05
1	E9DDB9
1	EA6D46
1	EAB24D
1	EAF8DC
1	EB200A
1	EB5C82
1	EB58EA
1	EB705C
1	EBB3F5
1	EBB8D0
1	EBCD65
1	EBE65A
1	EBDBAD
1	EBC6BA
1	EBCA44
1	EBC289
1	EB893E
1	EB9821
1	EBE6D6
1	EBFCD4
1	EC17BC
1	EC584C
1	EC623B
1	ED03A3
1	EDAAC0
1	EDFCF1
1	EDC854
1	EEDA9F
1	3BC48
1	EF0A80
1	7
1	EF06A5
1	EF04AD
1	EF0120
1	EF000F
1	EEFD0D
1	EEFB22
1	EEF8D8
1	EEF614
1	EEF43E
1	EEF206
1	EEF0FB
1	EEED81
1	EEEC2E
1	EEEA71
1	EEE8DA
1	EEE5C8
1	EEE409
1	EEE26A
1	EEDF68
1	EEDEA3
1	EEDC21
1	EEDA55
1	EED844
1	EED754
1	EED3F1
1	EED2AC
1	EED0D5
1	EEDAD2
1	EF69A6
1	F2F311
1	F4780B
1	F6ED29
1	F834B3
1	FA1C24
1	FAF4D5
1	FD0C49
1	FE0983
1	FF5784
1	78FA
1	E253
1	1042B
1	11F9F
1	14342
1	1178A
1	CC40
1	815C

Stop! Let Hand Rest...

Prepare to Close Hand...
3..
2...
1...
Start!

0	FE7D2
0	FB8FD
0	E2D34
0	F34C7
0	FE4F8
0	E4142
0	D62FE
0	F31B9
0	FBC73
0	E5F5C
0	F36F7
0	FDF7E
0	FBCF3
0	DA17A
0	F3A36
0	FBD3E
0	E8EE8
0	DC139
0	FDA45
0	FBE9A
0	DF673
0	F54EB
0	7DFC9
0	ED806
0	E4D35
0	FD5F3
0	FC147
0	EB3BC
0	FA7FA
0	FD261
0	F0BD9
0	EC11B
0	FCFBB
0	FBA89
0	EACB6
0	FA06F
0	FCD22
0	EFAD2
0	EA940
0	FCAAE
0	FB2D9
0	EEC5D
0	F967B
0	FC82B
0	EEB7F
0	E96DE
0	F92AD
0	FAB11
0	EDFEE
0	F8C20
0	FC2E3
0	ED911
0	E860D
0	F8800
0	FA1AE
0	ECDB1
0	F7DDD
0	FBD98
0	EC8BD
0	E70DF
0	F7B79
0	F9866
0	EBBC0
0	F7078
0	FB891
0	F95E9
0	E60B1
0	F6F0C
0	F8FBF
0	EAD4C
0	E4FA1
0	FB35E
0	F8B9E
0	E4C9F
0	F62D7
0	F874F
0	E9E79
0	E3ACD
0	FAE6C
0	F818A
0	E2E6A
0	F51F2
0	FABD4
0	E88E9
0	E2465
0	FA905
0	F7592
0	E189C
0	F4027
0	FA63F
0	E7927
0	E1527
0	FA395
0	F6AE1
0	E6AA4
0	F3378
0	FA0AA
0	E69E5
0	E0435
0	F2DE2
0	F65DD
0	E6B7D
0	C00000
0	F9BA4
0	F5BDA
0	DEEF8
0	F1FCD
0	F54F9
0	E4BA5
0	DDD09
0	F95CB
0	F4EA0
0	DD1DC
0	F0AC7
0	F9331
0	E378B
0	DCC17
0	F9034
0	F40F6
0	E2C34
0	EF556
0	F8CE5
0	E25A3
0	DB342
0	EEF0A
0	F365D
0	E1B32
0	DA2B4
0	F871F
0	F2FFB
0	D9CF3
0	EDDBC
0	F8423
0	E054B
0	D8E9A
0	F8096
0	F1D7D
0	DF6FC
0	EC0DE
0	F7CC5
0	DF1B8
0	D7CC8
0	EBE75
0	F1113
0	DEA16
0	EB510
0	F757A
0	F0464
0	D6631
0	EA7CF
0	F713F
0	DDB29
0	D65C8
0	F6CB4
0	EF94B
0	DCED1
0	E9AC1
0	F68E0
0	EF2B7
0	D5A97
0	E9104
0	EE5F1
0	DBFDB
0	D4C09
0	F5D78
0	EE1B9
0	700000
0	E7F99
0	F575C
0	DAD37
0	D3E88
0	F5101
0	ECD07
0	DA771
0	E732A
0	F4BEF
0	EBED6
0	D2D5D
0	E6DA7
0	F131A
0	F8498
0	F9BFF
0	D6323
0	CA27C
0	B7580
0	A5FA3
0	8888C
0	79751
0	47DB3
0	34769
0	2C0AA
0	1DF2C
0	16973
0	17838
0	1B470
0	19265
0	1E612
0	2331C
0	20A74
0	105A7
0	AB8A
0	470A
0	FFB92C
0	FE9240
0	FE2731
0	FD0E6C
0	FCA62C
0	FCCBA5
0	FCD079
0	FC6CA2
0	FC9B8B
0	FC9AA6
0	FC408D
0	FC6A85
0	FCF558
0	FD0538
0	FD95F4
0	FE253B
0	FEE264
0	FF55FA
0	FFA2CA
0	FF9ECE
0	FFA39F
0	B30D
0	149F6
0	2405F
0	27D48
0	249A1
0	24F8E
0	24C66
0	24B7F
0	2485B
0	24642
0	243F7
0	242EC
0	23F25
0	23DB0
0	23C0D
0	23A5E
0	236FF
0	23654
0	233D0
0	231DF
0	22FE7
0	22F19
0	22B70
0	22A23
0	228BA
0	2270C
0	223D2
0	22345
0	220E9
0	21EF1
0	21D0B
0	21C44
0	218CD
0	2177E
0	21641
0	214A9
0	2119D
0	21109
0	20EB4
0	20CDB
0	21BBB
0	17BEF
0	F9125A
0	F4E3B0
0	F2A8CA
0	EE1899
0	EC0EA7
0	E8E4A9
0	E80D04
0	E76CD3
0	E784E0
0	E76A89
0	E755DB
0	E78F71
0	E8326E
0	E8848B
0	E97B9A
0	E9E555
0	EA3732
0	EAB721
0	EBD736
0	EB9D67
0	EB9551
0	EB9F79
0	EB5014
0	EAC38C
0	EAD1F4
0	EA83F2
0	EA3BF7
0	E9D11F
0	E90A5F
0	E8E6FA
0	E958B2
0	E97FF9
0	E93CBF
0	E95F19
0	E9E9D0
0	E9BFCE
0	E9B14E
0	E9F2D0
0	EA0CEE
0	3A85FF
0	EA695E
0	EAF304
0	EB3E8A
0	EC67DA
0	ECD161
0	ED21B7
0	ED7637
0	EE40CA
0	EE7FCC
0	EEF4DB
0	EFB3D3
0	EFCDF5
0	F00410
0	F047F5
0	F0505D
0	F02562
0	F03EB7
0	F050F9
0	F03860
0	F05D67
0	F0CDF3
0	F0CAF7
0	F0FA40
0	F1C19C
0	F23D88
0	F46983
0	F603C3
0	F8D34B
0	F9E11E
0	FAAAF9
0	F99189
0	F56ABF
0	F1C1AD
0	F19F61
0	F198F8
0	F1979D
0	F1961C

Stop! Let Hand Rest...

Prepare to Open Hand...
3..
2...
1...
Start!

1	F22E37
1	F282E0
1	F40218
1	F33F16
1	F22A91
1	F3E78F
1	F4B290
1	F227C3
1	F271F3
1	F49716
1	F31D3A
1	F22408
1	F3B009
1	F46677
1	F2200C
1	F262B8
1	F45262
1	F2F285
1	F25A58
1	F38BF7
1	F44448
1	F21B3A
1	F25020
1	F4292D
1	F2DA87
1	F24ADF
1	F3655B
1	F2D6DF
1	F21651
1	F34E96
1	F40AA3
1	F2CFFB
1	F23A83
1	F33B62
1	F2B9C5
1	F21098
1	F31E4A
1	F3AF71
1	F20D99
1	F230A9
1	F31049
1	F28DF2
1	F20B89
1	F2FD0A
1	F38DE4
1	F208F7
1	F223B9
1	F37CF9
1	F278B6
1	F80000
1	F2DD04
1	F37086
1	F20439
1	F217C0
1	F357D9
1	F26513
1	F215C0
1	F2C364
1	F264BB
1	F20091
1	F2A988
1	F3322F
1	F25514
1	F209C8
1	F2937B
1	F247D3
1	F1FC8C
1	F28608
1	F302B5
1	F1FAD5
1	F20343
1	F27D2C
1	F2369F
1	F1F87A
1	F26F9A
1	F2E536
1	F1F688
1	F1FCEF
1	F2DB1B
1	F22A44
1	F1F470
1	F25591
1	F2C594
1	F1F2E7
1	F1F6B9
1	F2B9F5
1	F21A1E
1	F1F39A
1	F2443F
1	F2A903
1	F1EE7B
1	F1F062
1	F28811
1	F22FEC
1	F1CCC2
1	F0F5CB
1	EEB4B5
1	EDB84C
1	ECAB03
1	EBF4CF
1	EA3177
1	E99016
1	E88F7E
1	E73A51
1	E6C4E3
1	E616AF
1	E5E2E2
1	E56F54
1	E5648F
1	E53AC3
1	E518AB
1	E52632
1	E52825
1	E4D9A7
1	E4D3B8
1	E4E810
1	E4BBEA
1	E456DC
1	E4476A
1	E3F721
1	E3E6CB
1	E3FE6F
1	E3BB0B
1	E38070
1	E32936
1	E2FF3D
1	E27048
1	E24818
1	E1EB0F
1	E1870E
1	E0F010
1	E0EA97
1	E0D6CC
1	E0DEE9
1	E15BD7
1	E174B0
1	E176B1
1	E1CD3A
1	E1DBE1
1	E1C42C
1	E1E7EF
1	E25201
1	E26DBC
1	E2E291
1	E31E8F
1	E2CF01
1	E28F5B
1	E26CF8
1	E23361
1	E13FA6
1	E0D35E
1	DFE3B5
1	DFB40E
1	DFB827
1	DFB699
1	DFB4C6
1	DFB0EB
1	DFB00C
1	DFAD9E
1	DFAB7E
1	DFA8F6
1	DFA838
1	DFA495
1	DFA2F4
1	DFA175
1	DF9FEA
1	DF9C38
1	C00000
1	DF9940
1	DF9582
1	DF94C0
1	DF9288
1	DF9069
1	DF8E00
1	DF8D4C
1	DF8994
1	DF87F1
1	DF867B
1	DF84F7
1	DF8128
1	DF805D
1	DF7E1C
1	DF7C03
1	DF79A0
1	DF78E5
1	DFB2EF
1	DFC204
1	DF4EEC
1	DE6BAF
1	DDCE4E
1	DC6492
1	DBDF41
1	DAF493
1	DA840A
1	D918C3
1	D873AA
1	D7B9A2
1	D78A75
1	D78751
1	D7E357
1	D8FC3C
1	D95
1	D99437
1	D9E144
1	DA1961
1	DA0DDC
1	DA7E2D
1	DAB6D8
1	DAA18A
1	DAC977
1	DAEBBD
1	DA64EC
1	DA496A
1	DA48DE
1	DA2422
1	DA1EF4
1	DA561F
1	DA53B5
1	DA409E
1	DA8CEF
1	DA9D70
1	DA8788
1	DABCC7
1	DB9C7D
1	DBE380
1	DC7959
1	DCF9FB
1	DDC77C
1	DE7357
1	DEE24A
1	DF89B5
1	DFCCD7
1	E0A828
1	E10F1D
1	E18D95
1	E1F207
1	E2DC26
1	E324AB
1	E3B60F
1	E4230A
1	E4BD19
1	E4F0F4
1	E5ADC1
1	E64E4C
1	E68B85
1	E75351
1	E7A9B4
1	E7FD73
1	E84245
1	E8FE54
1	E93939
1	E9C1E6
1	EA30BF
1	EADAD5
1	EB16D8
1	EBDE3D
1	EC3E00
1	EC9CEE
1	ED2B71
1	ED7302
1	EDB6D0
1	EDEC9D
1	EDB920
1	ED4F08
1	ED0018
1	ED51F4
1	EDEE06
1	EE544F
1	EF7907
1	F00BEA
1	F0B0F4
1	F148C1
1	F1D078
1	F1E4D2
1	F1E3EA
1	F1E1F4
1	F1E053
1	F1DC8B
1	F1DBA4
1	F1D95D
1	F1D763
1	F1D4F1
1	F1D43D
1	F1D0FA
1	F1CF5F
1	F1CDF3
1	F1CC9B
1	F1C921
1	F1C864
1	F1C692
1	F1C4AE
1	F1C268
1	F1C1D7
1	F1BEBB
1	F1BC6C
1	F1BBD5
1	F1B8AF
1	F1B724
1	F1AEF0
1	F0E57D
1	EFCCEF
1	EF72C3
1	EE0E66
1	ECF7AD
1	EBFA45
1	EBE030
1	EB75AB
1	EB6F59
1	EBC80D
1	EBC7C0
1	EBB1C8
1	EBE16D
1	EBE5D5
1	EBCB9D
1	EBE514
1	EC1CAB
1	EC1D98
1	EC8A4E
1	ECD683
1	ED28E4
1	ED7490
1	EE51D7
1	EEA79B
1	EF748C
1	F0115A
1	F1100C
1	F15AD3
1	F228A9
1	F29780
1	F32949
1	F3B93B
1	F3F5A6
1	F4293D

Stop! Let Hand Rest...

Prepare to Close Hand...
3..
2...
1...
Start!
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

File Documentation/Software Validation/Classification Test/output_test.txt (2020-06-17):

>> output_test

output_test =

  122×1 cell array

    {'Right Hand' }
    {' Rest'      }
    {' Rest'      }
    {' Right Hand'}
    {' Right Hand'}
    {' Right Hand'}
    {' Right Hand'}
    {' Right Hand'}
    {' Right Hand'}
    {' Right Hand'}
    {' Rest'      }
    {' Right Hand'}
    {' Rest'      }
    {' Rest'      }
    {' Right Hand'}
    {' Rest'      }
    {' Right Hand'}
    {' Right Hand'}
    {' Right Hand'}
    {' Right Hand'}
    {' Rest'      }
    {' Right Hand'}
    {' Rest'      }
    {' Right Hand'}
    {' Right Hand'}
    {' Right Hand'}
    {' Rest'      }
    {' Rest'      }
    {' Right Hand'}
    {' Right Hand'}
    {' Rest'      }
    {' Rest'      }
    {' Right Hand'}
    {' Right Hand'}
    {' Rest'      }
    {' Rest'      }
    {' Rest'      }
    {' Rest'      }
    {' Rest'      }
    {' Right Hand'}
    {' Right Hand'}
    {' Rest'      }
    {' Rest'      }
    {' Right Hand'}
    {' Rest'      }
    {' Rest'      }
    {' Rest'      }
    {' Rest'      }
    {' Right Hand'}
    {' Rest'      }
    {' Right Hand'}
    {' Right Hand'}
    {' Right Hand'}
    {' Right Hand'}
    {' Rest'      }
    {' Right Hand'}
    {' Rest'      }
    {' Rest'      }
    {' Rest'      }
    {' Right Hand'}
    {' Right Hand'}
    {' Rest'      }
    {' Right Hand'}
    {' Rest'      }
    {' Rest'      }
    {' Right Hand'}
    {' Rest'      }
    {' Right Hand'}
    {' Rest'      }
    {' Right Hand'}
    {' Rest'      }
    {' Right Hand'}
    {' Rest'      }
    {' Rest'      }
    {' Rest'      }
    {' Rest'      }
    {' Right Hand'}
    {' Right Hand'}
    {' Right Hand'}
    {' Rest'      }
    {' Right Hand'}
    {' Rest'      }
    {' Rest'      }
    {' Rest'      }
    {' Right Hand'}
    {' Rest'      }
    {' Rest'      }
    {' Right Hand'}
    {' Right Hand'}
    {' Right Hand'}
    {' Rest'      }
    {' Right Hand'}
    {' Right Hand'}
    {' Right Hand'}
    {' Rest'      }
    {' Right Hand'}
    {' Rest'      }
    {' Rest'      }
    {' Right Hand'}
    {' Right Hand'}
    {' Rest'      }
    {' Rest'      }
    {' Rest'      }
    {' Right Hand'}
    {' Rest'      }
    {' Right Hand'}
    {' Rest'      }
    {' Right Hand'}
    {' Rest'      }
    {' Right Hand'}
    {' Right Hand'}
    {' Right Hand'}
    {' Right Hand'}
    {' Rest'      }
    {' Rest'      }
    {' Rest'      }
    {' Right Hand'}
    {' Right Hand'}
    {' Rest'      }
    {' Rest'      }
    {' Rest'      }
    {' Right Hand'}

>>

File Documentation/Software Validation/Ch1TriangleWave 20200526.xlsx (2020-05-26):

51F36 | 35990 | 3855B | 4EE1C | 1FE7C | 44776 | 2DF0F | F5B09 | 335670 | 219536 | 230747 | 323100 | 130684 | 280438 | 188175 | 1006345
53725 | 359FE | 385CA | 4EE97 | 1FEEF | 447F6 | 2DF88 | F5B94 | 341797 | 219646 | 230858 | 323223 | 130799 | 280566 | 188296 | 1006484
54D64 | 358000 | 384AD | 4ED8A | 1FDD6 | 446F2 | 2DE7B | F5A97 | 347492 | 3506176 | 230573 | 322954 | 130518 | 280306 | 188027 | 1006231
563EC | 35850 | 3841F | 4ED03 | 1FD48 | 44670 | 2DDF4 | F5A2A | 353260 | 219216 | 230431 | 322819 | 130376 | 280176 | 187892 | 1006122
57000 | 164 | ECC0D6 | 66800 | 5CC13B | 98C07F | A50111 | F880B7 | 356352 | 356 | 15515862 | 419840 | 6078779 | 10010751 | 10813713 | 16285879
5AB94 | 35A0B | 385000000 | 4EEDB | 1FF08 | 44862 | 2DFCC | F5C4A | 371604 | 219659 | 15116271616 | 323291 | 130824 | 280674 | 188364 | 1006666
5C1B7 | 3580000 | 384C1 | 4EDC4 | 1FDE6 | 44754 | 2DEB3 | F5B44 | 377271 | 56098816 | 230593 | 323012 | 130534 | 280404 | 188083 | 1006404
5D826 | 3584D | 3842B | 4ED39 | 1FD51 | 446D2 | 2DE28 | F5AD3 | 383014 | 219213 | 230443 | 322873 | 130385 | 280274 | 187944 | 1006291
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

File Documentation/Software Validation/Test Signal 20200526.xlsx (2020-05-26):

FFF330 | FFF280 | FFF303 | FFF2A3 | FFF25D | FFF368 | FFF2BC | FFF2E8 | 16773936 | 16773760 | 16773891 | 16773795 | 16773725 | 16773992 | 16773820 | 16773864
FFEEA7 | FFEDF2 | FFEE74 | FFEE16 | FFEDD0 | FFEED8 | FFEE32 | FFEE5A | 16772775 | 16772594 | 16772724 | 16772630 | 16772560 | 16772824 | 16772658 | 16772698
FFEEA7 | FFEDF1 | FFEE76 | FFEE15 | FFEDD1 | FFEED9 | FFEE31 | FFEE5B | 16772775 | 16772593 | 16772726 | 16772629 | 16772561 | 16772825 | 16772657 | 16772699
FFEEA7 | FFEDF3 | FFEE74 | FFEE13 | FFEDD4 | FFEEDC | FFEE33 | FFEE5C | 16772775 | 16772595 | 16772724 | 16772627 | 16772564 | 16772828 | 16772659 | 16772700
FFEEA8 | FFEDF3 | FFEE74 | FFEE15 | FFEDD1 | FFEEDB | FFEE31 | FFEE60 | 16772776 | 16772595 | 16772724 | 16772629 | 16772561 | 16772827 | 16772657 | 16772704
FFEEA7 | FFEDF2 | FFEE77 | FFEE15 | FFEDD2 | FFEEDB | FFEE31 | FFEE5C | 16772775 | 16772594 | 16772727 | 16772629 | 16772562 | 16772827 | 16772657 | 16772700
FFEEA9 | FFEDEF | FFEE78 | FFEE15 | FFEDD4 | FFEEDE | FFEE2C | FFEE59 | 16772777 | 16772591 | 16772728 | 16772629 | 16772564 | 16772830 | 16772652 | 16772697
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

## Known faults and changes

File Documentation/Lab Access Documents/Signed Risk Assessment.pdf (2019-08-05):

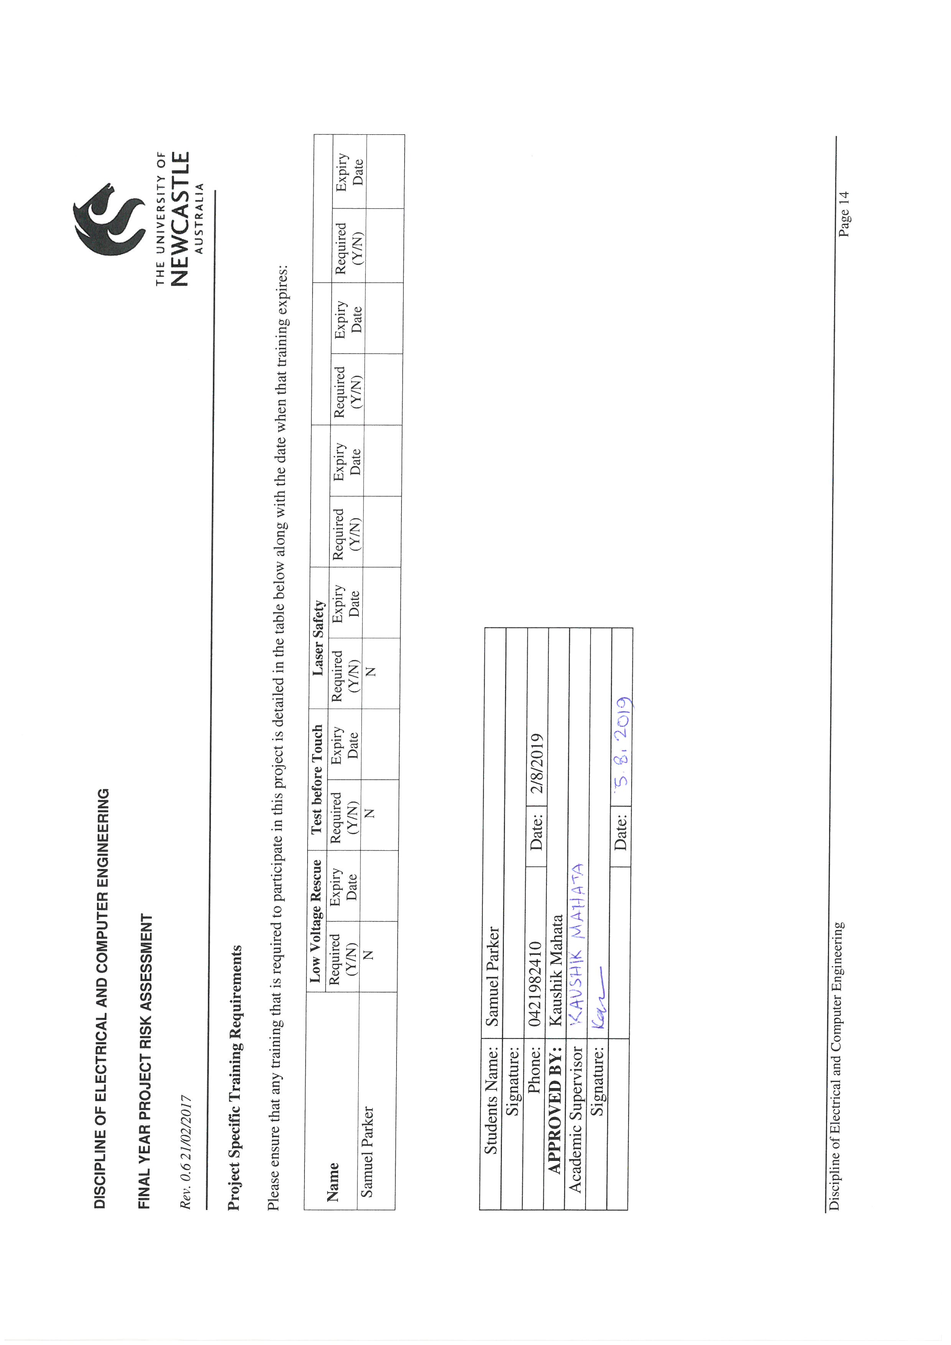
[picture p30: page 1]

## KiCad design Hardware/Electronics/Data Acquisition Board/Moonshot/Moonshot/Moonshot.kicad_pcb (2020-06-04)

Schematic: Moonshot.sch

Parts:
A1: Arduino_Nano_v2.x; Arduino_Nano
ADC1: ADS1299-Board
C1, C5: 10u; C_0603_1608Metric_Pad1.05x0.95mm_HandSolder
C2, C4: 1u; C_0603_1608Metric_Pad1.05x0.95mm_HandSolder
C3: 100n; C_0603_1608Metric_Pad1.05x0.95mm_HandSolder
D1: 7.5V; D_SMA_Handsoldering
J1: Barrel_Jack; BarrelJack_CUI_PJ-063AH_Horizontal
J2: Conn_01x06_Female; HC-05
J3, J4, J5, J6, J7, J8, J9, J10, J11: Conn_01x01_Male; DIN 42802-1
Q1: DMP2100U; SOT-23
R1: 33k; R_0603_1608Metric_Pad1.05x0.95mm_HandSolder
R2, R3, R4, R5: 1k; R_0603_1608Metric_Pad1.05x0.95mm_HandSolder
R6, R7, R8, R9: 2k; R_0603_1608Metric_Pad1.05x0.95mm_HandSolder
U2: MCP1755T-5002E_SOT223-5; SOT-223-6

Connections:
/+3V3: A1.17 (3V3), ADC1.5, ADC1.6
/+5V: C3.1, C4.1, C5.1, J2.5, U2.4
/BT_RX_3V3: A1.11 (D8), J2.3
/BT_TX_3V3: J2.2, R2.1, R6.1
/BT_TX_5V: A1.12 (D9), R2.2
/GND: A1.4 (GND), A1.29 (GND), ADC1.2, ADC1.8, C1.2, C2.2, C3.2, C4.2, C5.2, J1.2, J2.4, R1.2, R6.2, R7.2, R8.2, R9.2, U2.3, U2.5, U2.6
/LED: A1.6 (D3)
/MISO_3V3: A1.15 (D12), ADC1.11
/MOSI_3V3: ADC1.4, R4.1, R8.1
/MOSI_5V: A1.14 (D11), R4.2
/SCLK_3V3: ADC1.10, R3.1, R7.1
/SCLK_5V: A1.16 (D13), R3.2
/V+: A1.30 (VIN), ADC1.1, C1.1, C2.1, D1.1, Q1.2, U2.1, U2.2
/~CS_3V3: ADC1.9, R5.1, R9.1
/~CS_5V: A1.7 (D4), R5.2
/~DRDY_3V3: A1.9 (D6), ADC1.12
unnamed: ADC1.21, J11.1
unnamed: ADC1.22, J10.1
unnamed: ADC1.23, J9.1
unnamed: ADC1.24, J8.1
unnamed: ADC1.25, J7.1
unnamed: ADC1.26, J6.1
unnamed: ADC1.27, J5.1
unnamed: ADC1.28, J4.1
unnamed: ADC1.29, J3.1
unnamed: D1.2, Q1.1, R1.1
unnamed: J1.1, Q1.3

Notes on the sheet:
LED
GND
+5V
STATE

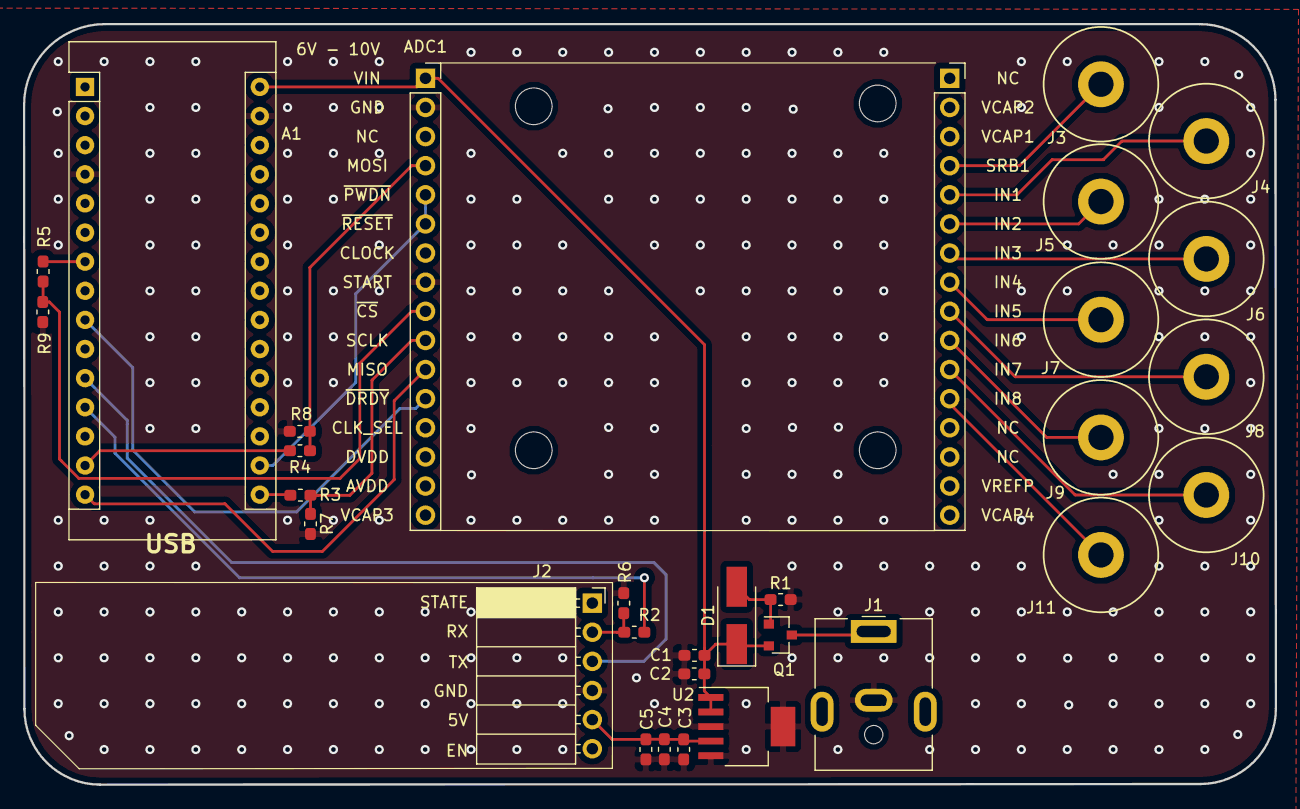
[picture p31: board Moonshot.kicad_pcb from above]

Board: 2 copper layers, 109.2 x 66.3 mm, 34 parts (0 on the bottom side), 26 nets.

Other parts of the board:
 : MountingHole_3.2mm_M3
 #2,  #3,  #4: MountingHole_3.2mm_M3

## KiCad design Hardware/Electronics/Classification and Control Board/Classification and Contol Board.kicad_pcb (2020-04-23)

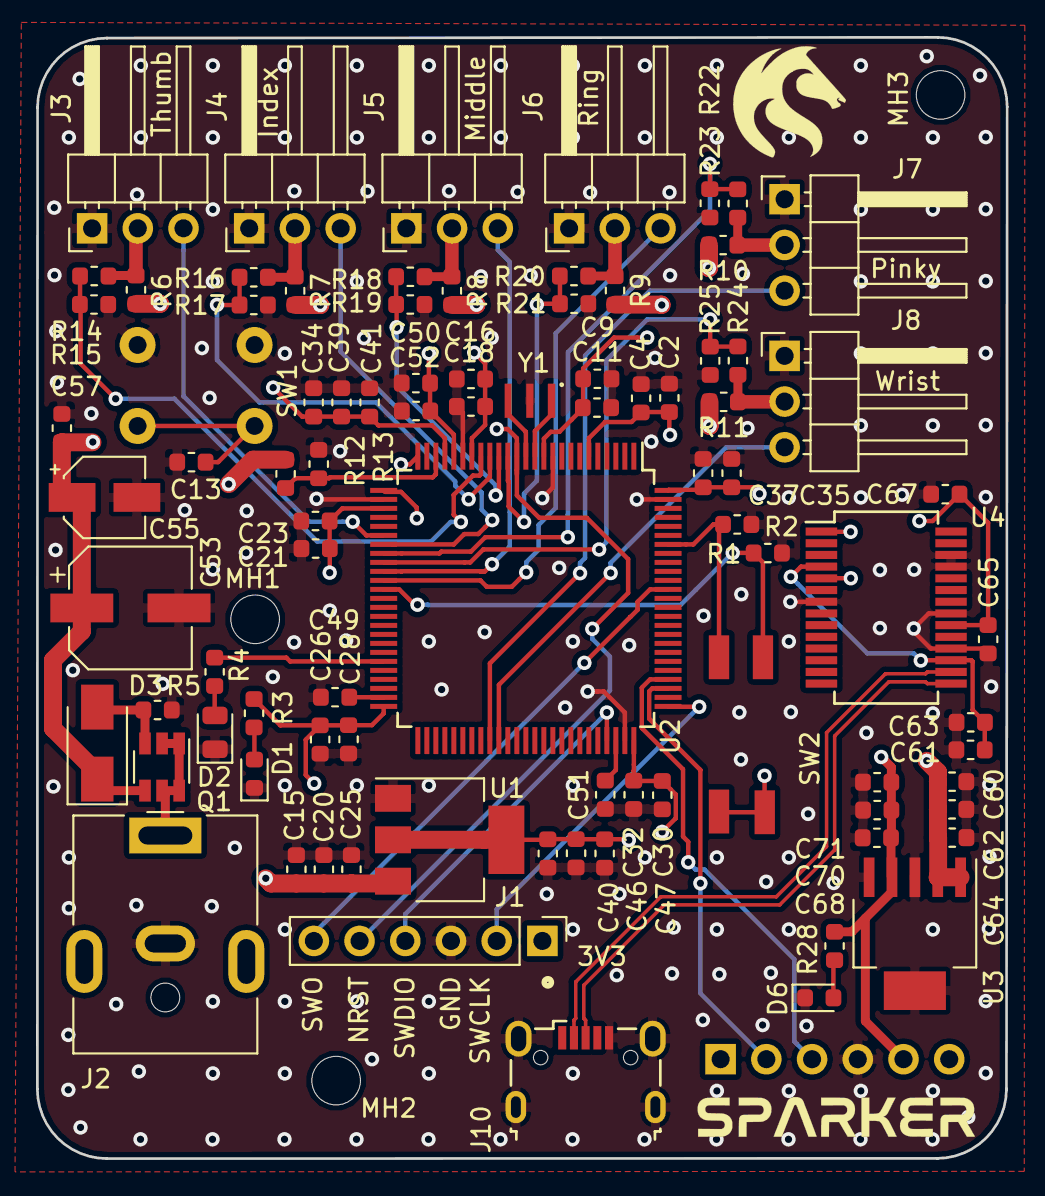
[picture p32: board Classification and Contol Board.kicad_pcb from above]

Board: 4 copper layers, 53.9 x 62.3 mm, 94 parts (1 on the bottom side), 46 nets.

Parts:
C2, C9, C16, C21, C26, C30, C35, C39, C61, C62, C67, C70: 100n; C_0603_1608Metric
C4, C11, C18, C20, C23, C28, C32, C34, C37, C46, C52, C63, C64, C65, C71: 10n; C_0603_1608Metric
C13: 0.1u; C_0603_1608Metric
C15, C47, C57, C60, C68: 4.7u; C_0603_1608Metric
C25, C40: 1n; C_0603_1608Metric
C41, C50: 1u; C_0603_1608Metric
C49, C51: 2.2u; C_0603_1608Metric
C53: 100u; CP_Elec_6.3x7.7
C55: 10u; CP_Elec_4x5.4
D1: LTST-C171TGKT; LED_0603_1608Metric
D2: LO R976-PS-1; LED_0805_2012Metric
D3: 10V; D_SMA
D6: LED; LED_0603_1608Metric
J1: SWD Header; PinHeader_1x06_P2.54mm_Vertical
J2: Barrel_Jack; BarrelJack_CUI_PJ-063AH_Horizontal
J3: Thumb; PinHeader_1x03_P2.54mm_Horizontal
J4: Index; PinHeader_1x03_P2.54mm_Horizontal
J5: Middle; PinHeader_1x03_P2.54mm_Horizontal
J6: Ring; PinHeader_1x03_P2.54mm_Horizontal
J7: Pinky; PinHeader_1x03_P2.54mm_Horizontal
J8: Wrist; PinHeader_1x03_P2.54mm_Horizontal
J9: HC05; HC-05
J10: USB_B_Mini; USB_Micro-B_Wuerth_629105150521
LOGO1: SparkerLogo; NASA_small
LOGO2: UoNLogo; UoN
MH1, MH2, MH3: MountingHole; MountingHole_2.7mm_M2.5
Q1: SQ3425EV-T1_GE3; TSOT-23-6
R1, R2, R13, R15, R17, R19, R21, R23, R25: 100k; R_0603_1608Metric
R3: 6R; R_0603_1608Metric
R4: 68R; R_0603_1608Metric
R5: 33k; R_0603_1608Metric
R6, R7, R8, R9, R10, R11: 50m; R_0603_1608Metric
R12, R14, R16, R18, R20, R22, R24: 500k; R_0603_1608Metric
R28: 150; R_0603_1608Metric
SW1: SW_Push; 1825910-6
SW2: SW_DIP_x02; DIP-Switch_01x02
U1: LDL1117S33R; SOT-223-3_TabPin2
U2: STM32F407VGTx; LQFP-100_14x14mm_P0.5mm
U3: MCP1755T-5002E_SOT223-5; SOT-223-6
U4: FT232RL; SSOP-28_5.3x10.2mm_P0.65mm
Y1: 8MHz; CSTNE12M0GH5L000R0

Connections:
/Communications/+5V: C65.1, C67.1, C68.1, C70.1, C71.1, J9.5, R28.2, U3.4, U4.20
/Communications/BT_RX: J9.3, U2.79
/Communications/BT_TX: J9.2, U2.78
/Communications/D+: J10.3, U4.15
/Communications/D-: J10.2, U4.16
/Communications/RX: U2.26, U4.5
/Communications/TX: U2.25, U4.1
/Control/FB1: R14.2, R15.1, U2.18
/Control/FB2: R16.2, R17.1, U2.17
/Control/FB3: R18.2, R19.1, U2.16
/Control/FB4: R20.2, R21.1, U2.15
/Control/FB5: R22.2, R23.1, U2.33
/Control/FB6: R24.2, R25.1, U2.34
/Control/FB_REF: R12.2, R13.1, U2.23
/Control/VSER1: J3.2, R6.1, R14.1
/Control/VSER2: J4.2, R7.1, R16.1
/Control/VSER3: J5.2, R8.1, R18.1
/Control/VSER4: J6.2, R9.1, R20.1
/Control/VSER5: J7.2, R10.1, R22.1
/Control/VSER6: J8.2, R11.1, R24.1
/GND: C2.2, C4.2, C9.2, C11.2, C13.2, C15.2, C16.2, C18.2, C20.2, C21.2, C23.2, C25.2, C26.2, C28.2, C30.2, C32.2, C34.2, C35.2, C37.2, C39.2, C40.2, C41.2, C46.2, C47.2, C49.2, C50.2, C51.2, C52.2, C53.2, C55.2, C57.2, C60.2, C61.2, C62.2, C63.2, C64.2, C65.2, C67.2, C68.2, C70.2, C71.2, D1.1, D2.1, D6.1, J1.3, J2.2, J3.1, J4.1, J5.1, J6.1, J7.1, J8.1, J9.4, J10.5, J10.6, R1.2, R2.2, R5.2, R13.2, R15.2, R17.2, R19.2, R21.2, R23.2, R25.2, SW1.1, SW1.2, U1.1, U2.10, U2.20, U2.27, U2.74, U2.99, U3.3, U3.5, U3.6, U4.7, U4.18, U4.21, U4.25, U4.26, Y1.2
/STM32F407VGTx/3V3: C2.1, C4.1, C9.1, C11.1, C16.1, C18.1, C21.1, C23.1, C26.1, C28.1, C30.1, C32.1, C34.1, C35.1, C37.1, C39.1, C40.1, C41.1, C46.1, C47.1, C50.1, C52.1, J1.1, R3.2, SW2.3, SW2.4, U1.2, U2.6, U2.11, U2.19, U2.21, U2.22, U2.28, U2.50, U2.75, U2.100
/STM32F407VGTx/BOOT0: R1.1, SW2.2, U2.94
/STM32F407VGTx/BOOT1: R2.1, SW2.1, U2.37
/STM32F407VGTx/NRST: C13.1, J1.5, SW1.3, SW1.4, U2.14
/STM32F407VGTx/PWM1: J3.3, U2.31
/STM32F407VGTx/PWM2: J4.3, U2.32
/STM32F407VGTx/PWM3: J5.3, U2.35
/STM32F407VGTx/PWM4: J6.3, U2.36
/STM32F407VGTx/PWM5: J7.3, U2.59
/STM32F407VGTx/PWM6: J8.3, U2.60
/STM32F407VGTx/SWCLK: J1.2, U2.76
/STM32F407VGTx/SWDIO: J1.4, U2.72
/STM32F407VGTx/SWO: J1.6, U2.89
/V+: C15.1, C20.1, C25.1, C53.1, C55.1, C57.1, C60.1, C62.1, C64.1, D3.1, Q1.4, R6.2, R7.2, R8.2, R9.2, R10.2, R11.2, R12.1, U1.3, U3.1, U3.2
unnamed: C49.1, U2.49
unnamed: C51.1, U2.73
unnamed: C61.1, C63.1, U4.4, U4.17
unnamed: D1.2, R3.1
unnamed: D2.2, R4.2
unnamed: D3.2, Q1.3, R5.1
unnamed: D6.2, R28.1
unnamed: J2.1, Q1.1, Q1.2, Q1.5, Q1.6
unnamed: R4.1, U2.45
unnamed: U2.12, Y1.1
unnamed: U2.13, Y1.3

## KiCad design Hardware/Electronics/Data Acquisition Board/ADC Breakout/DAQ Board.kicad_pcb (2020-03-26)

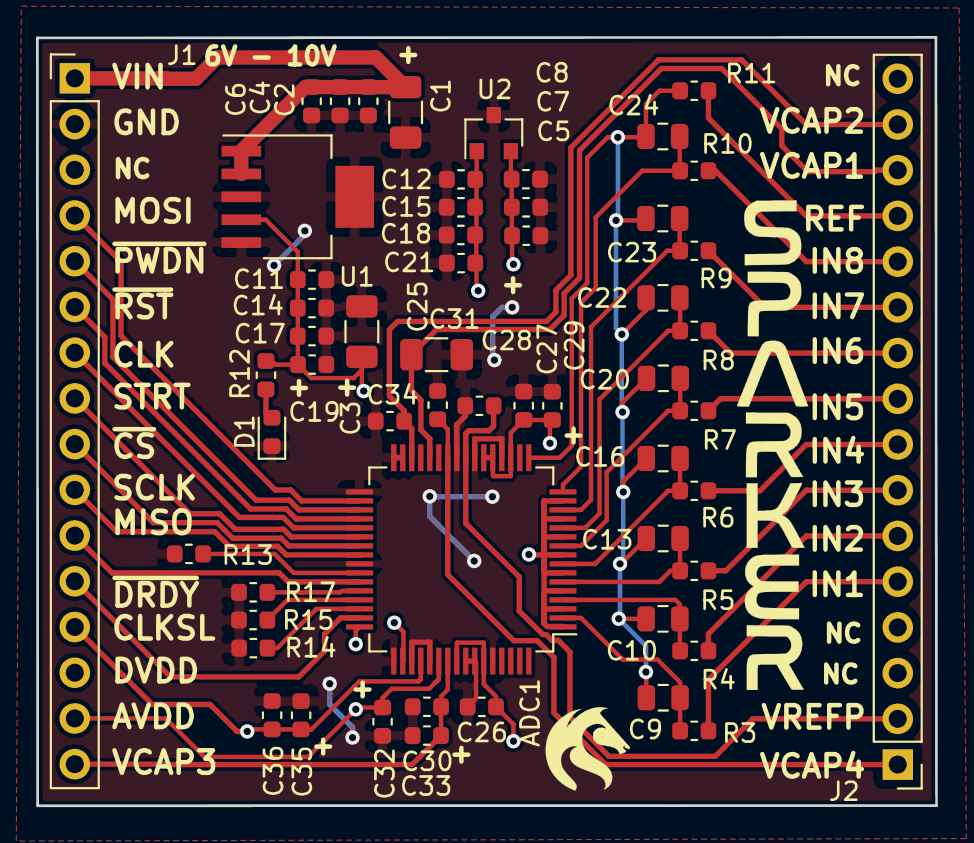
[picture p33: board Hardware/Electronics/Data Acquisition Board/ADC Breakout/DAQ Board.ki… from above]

Board: 2 copper layers, 50.0 x 42.7 mm, 56 parts (0 on the bottom side), 41 nets.

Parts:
ADC1: ADS1299-8; TQFP-64_10x10mm_P0.5mm
C1, C3, C31: 100uF; C_1206_3216Metric
C2, C5, C19, C21: 10uF; C_0603_1608Metric
C4, C7, C17, C18: 100nF; C_0603_1608Metric
C6, C8, C14, C15: 10nF; C_0603_1608Metric
C9, C10, C13, C16, C20, C22, C23, C24: 24nF; C_0805_2012Metric
C11, C12: 1nF; C_0603_1608Metric
C25, C26, C29, C32, C33, C34, C36: 1uF; C_0603_1608Metric
C27, C30, C35: 0.1uF; C_0603_1608Metric
C28: 10u; C_0603_1608Metric
D1: LTST-C194TBKT; LED_0603_1608Metric
J1, J2: Conn_01x16; PinHeader_1x16_P2.54mm_Vertical
R3, R4, R5, R6, R7, R8, R9, R10, R11: 220k; R_0603_1608Metric
R12: 100; R_0603_1608Metric
R13, R14, R15, R17: 33k; R_0603_1608Metric
U1: MCP1755T-5002E_SOT223-5; SOT-223-6
U2: LM3480-3.3; SOT-23

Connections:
/AVDD: ADC1.1, ADC1.3, ADC1.5, ADC1.7, ADC1.9, ADC1.11, ADC1.13, ADC1.15, ADC1.19, ADC1.21, ADC1.22, ADC1.54, ADC1.56, ADC1.59, C3.1, C5.1, C7.1, C8.1, C11.1, C14.1, C17.1, C19.1, C26.1, C27.2, C29.2, C32.2, J1.15, R12.2, U1.4, U2.2
/AVSS: ADC1.20, ADC1.23, ADC1.25, ADC1.31, ADC1.32, ADC1.33, ADC1.41, ADC1.49, ADC1.51, ADC1.53, ADC1.57, ADC1.58, ADC1.60, C1.2, C2.2, C3.2, C4.2, C5.2, C6.2, C7.2, C8.2, C11.2, C12.2, C14.2, C15.2, C17.2, C18.2, C19.2, C21.2, C25.2, C26.2, C27.1, C28.1, C29.1, C30.1, C31.2, C32.1, C33.1, C34.2, C35.2, C36.2, D1.1, J1.2, R13.2, R14.1, R15.1, R17.1, U1.3, U1.5, U1.6, U2.3
/CLK: ADC1.37, J1.7
/DVDD: ADC1.48, ADC1.50, ADC1.52, C12.1, C15.1, C18.1, C21.1, C35.1, C36.1, J1.13, J1.14, U2.1
/IN1: J2.5, R3.2
/IN2: J2.6, R4.2
/IN3: J2.7, R5.2
/IN4: J2.8, R6.2
/IN5: J2.9, R7.2
/IN6: J2.10, R8.2
/IN7: J2.11, R9.2
/IN8: J2.12, R10.2
/MISO: ADC1.43, J1.11
/MOSI: ADC1.34, J1.4
/REF: J2.13, R11.2
/SCLK: ADC1.40, J1.10
/START: ADC1.38, J1.8
/VCAP1: ADC1.28, C31.1, J2.14
/VCAP2: ADC1.30, C34.1, J2.15
/VCAP3: ADC1.55, C30.2, C33.2, J1.16
/VCAP4: ADC1.26, C25.1, J2.1
/VIN: C1.1, C2.1, C4.1, C6.1, J1.1, U1.1, U1.2
/VREFP: ADC1.24, C28.2, J2.2
/~CS: ADC1.39, J1.9
/~DRDY: ADC1.47, J1.12
/~PWDN: ADC1.35, J1.5
/~RESET: ADC1.36, J1.6
unnamed: ADC1.2, C9.1, R3.1
unnamed: ADC1.4, C10.1, R4.1
unnamed: ADC1.6, C13.1, R5.1
unnamed: ADC1.8, C16.1, R6.1
unnamed: ADC1.10, C20.1, R7.1
unnamed: ADC1.12, C22.1, R8.1
unnamed: ADC1.14, C23.1, R9.1
unnamed: ADC1.16, C24.1, R10.1
unnamed: ADC1.17, C9.2, C10.2, C13.2, C16.2, C20.2, C22.2, C23.2, C24.2, R11.1
unnamed: ADC1.42, R13.1
unnamed: ADC1.44, R17.2
unnamed: ADC1.45, R15.2
unnamed: ADC1.46, R14.2
unnamed: D1.2, R12.1

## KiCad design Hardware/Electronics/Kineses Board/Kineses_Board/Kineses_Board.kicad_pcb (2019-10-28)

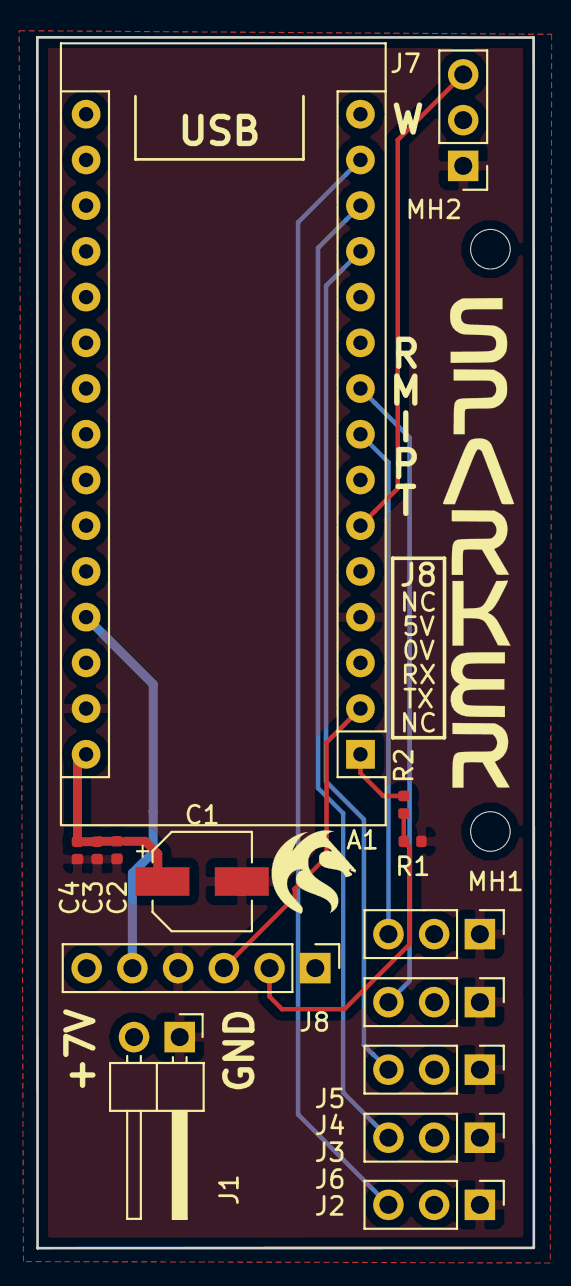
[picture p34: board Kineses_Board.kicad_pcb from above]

Board: 2 copper layers, 27.6 x 67.3 mm, 19 parts (0 on the bottom side), 12 nets.

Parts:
A1: Arduino_Nano_v3.x; Arduino_Nano
C1: 100u; CP_Elec_5x5.3
C2: 10u; C_0402_1005Metric
C3: 100n; C_0402_1005Metric
C4: 10n; C_0402_1005Metric
J1: Power; PinHeader_1x02_P2.54mm_Horizontal
J2: Thumb; PinHeader_1x03_P2.54mm_Vertical
J3: Index; PinHeader_1x03_P2.54mm_Vertical
J4: Middle; PinHeader_1x03_P2.54mm_Vertical
J5: Ring; PinHeader_1x03_P2.54mm_Vertical
J6: Pinky; PinHeader_1x03_P2.54mm_Vertical
J7: Wrist; PinHeader_1x03_P2.54mm_Vertical
J8: HC-05; PinHeader_1x06_P2.54mm_Vertical
LOGO1: SparkerLogo; NASA_Vertical
LOGO2: UoNLogo; UoN_Small
MH1, MH2: MountingHole; MountingHole_2.2mm_M2
R1: 2K; R_0402_1005Metric
R2: 1K; R_0402_1005Metric

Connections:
/+5V: A1.27, J8.5
/GND: A1.4, A1.29, C1.2, C2.1, C3.1, C4.1, J1.1, J2.1, J3.1, J4.1, J5.1, J6.1, J7.1, J8.4, R1.2
/Index: A1.12, J3.3
/Middle: A1.9, J4.3
/Pinky: A1.13, J6.3
/RX: A1.2, J8.3
/Ring: A1.8, J5.3
/TX: J8.2, R1.1, R2.1
/Thumb: A1.14, J2.3
/VIN: A1.30, C1.1, C2.2, C3.2, C4.2, J1.2, J2.2, J3.2, J4.2, J5.2, J6.2, J7.2
/Wrist: A1.6, J7.3
unnamed: A1.1, R2.2

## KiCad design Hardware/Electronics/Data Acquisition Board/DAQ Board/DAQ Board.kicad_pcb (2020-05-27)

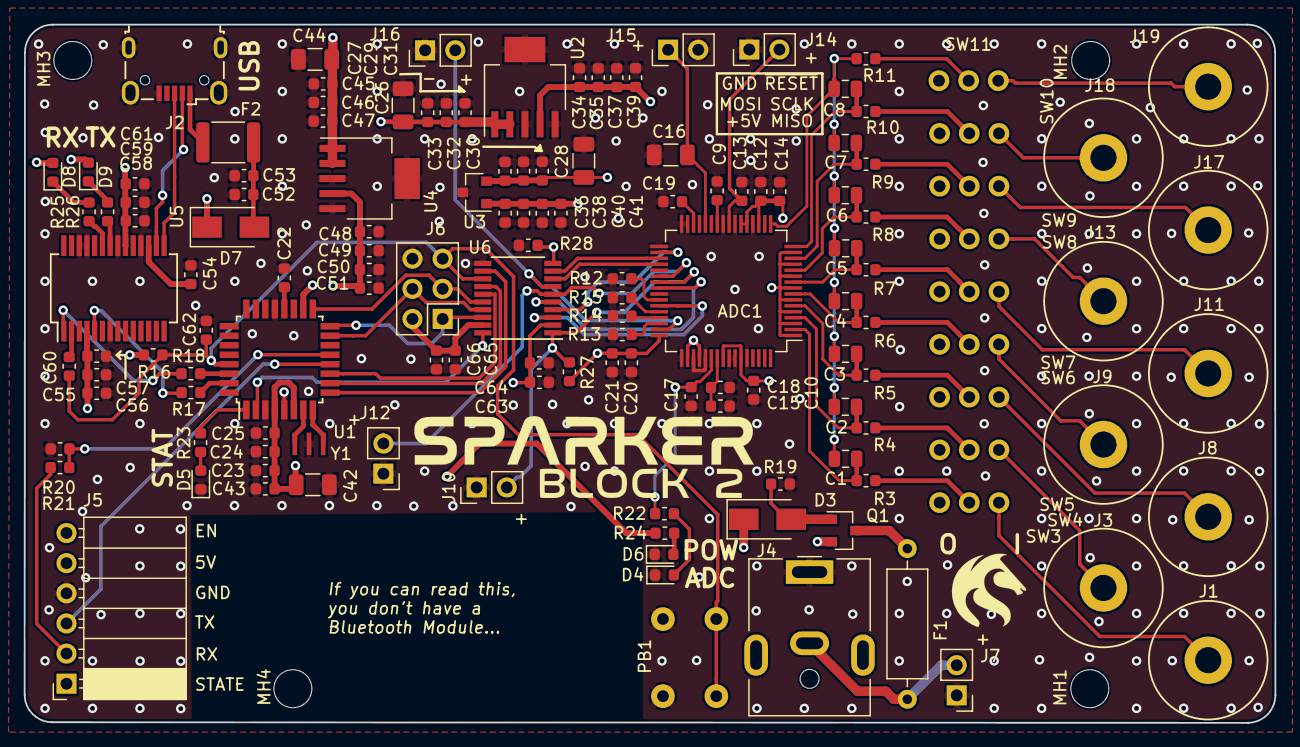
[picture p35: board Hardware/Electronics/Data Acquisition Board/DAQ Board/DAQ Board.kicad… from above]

Board: 4 copper layers, 105.4 x 58.9 mm, 145 parts (0 on the bottom side), 84 nets.

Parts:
ADC1: ADS1299-8; TQFP-64_10x10mm_P0.5mm
C1, C2, C3, C4, C5, C6, C7, C8: 24nF; C_0805_2012Metric
C9, C10, C14, C17, C18, C19, C21, C23, C25: 1uF; C_0603_1608Metric
C12, C15, C20: 0.1uF; C_0603_1608Metric
C13, C27, C30, C39, C41, C43, C45, C51, C55, C61, C62: 10uF; C_0603_1608Metric
C16, C26, C28, C42, C44: 100uF; C_1206_3216Metric
C22, C29, C32, C37, C40, C46, C50, C53, C54, C56, C59, C60: 100nF; C_0603_1608Metric
C24, C52: 4.7uF; C_0603_1608Metric
C31, C33, C35, C38, C47, C49, C57, C58: 10nF; C_0603_1608Metric
C34, C36, C48: 1nF; C_0603_1608Metric
C63, C66: 100n; C_0603_1608Metric
C64, C65: 10n; C_0603_1608Metric
D3: 7.5V; D_SMA
D4, D6: LTST-C194TBKT; LED_0603_1608Metric
D5, D9: LTST-C191KGKT; LED_0603_1608Metric
D7: B130-13-F; D_SMA
D8: LTST-C191KRKT; LED_0603_1608Metric
F1: 025101.5MAT1L; R_Axial_DIN0309_L9.0mm_D3.2mm_P12.70mm_Horizontal
F2: MF-MSMF050-2; Fuse_1812_4532Metric
J1, J3, J8, J9, J11, J13, J17, J18, J19: Conn_01x01_Male; DIN 42802-1
J2: USB_B_Mini; USB_Micro-B_Wuerth_629105150521
J4: DC Barrel Jack; BarrelJack_CUI_PJ-063AH_Horizontal
J5: HC-05 BT Module; HC-05
J6: ICSP Header; PinHeader_2x03_P2.54mm_Vertical
J7: VIN_RAW_TP; PinHeader_1x02_P2.54mm_Vertical
J10: ~CS~_TP; PinHeader_1x02_P2.54mm_Vertical
J12: START_TP; PinHeader_1x02_P2.54mm_Vertical
J14: VREFP_TP; PinHeader_1x02_P2.54mm_Vertical
J15: VCAP1_TP; PinHeader_1x02_P2.54mm_Vertical
J16: DRDY_TP; PinHeader_1x02_P2.54mm_Vertical
LOGO1: UoNLogo; UoN
LOGO2: SparkerLogo; NASA
LOGO3: VersionLogo; Block2
MH1, MH2, MH3, MH4: MountingHole; MountingHole_3.2mm_M3
PB1: TE-1825910-6; 1825910-6
Q1: DMP2100U; SOT-23
R3, R4, R5, R6, R7, R8, R9, R10, R11: 220k; R_0603_1608Metric
R12, R13, R14, R15, R19: 33k; R_0603_1608Metric
R16, R17, R18, R21: 1K; R_0603_1608Metric
R20: 2K; R_0603_1608Metric
R22, R23, R24, R25, R26: 100; R_0603_1608Metric
R27, R28: 100k; R_0603_1608Metric
SW3, SW4, SW5, SW6, SW7, SW8, SW9, SW10, SW11: SW_SPDT; SPDT-THT_Slide
U1: ATmega328P-AU; TQFP-32_7x7mm_P0.8mm
U2, U4: MCP1755T-5002E_SOT223-5; SOT-223-6
U3: LM3480-3.3; SOT-23
U5: FT232RL; SSOP-28_5.3x10.2mm_P0.65mm
U6: TXS0108EPWR; TSSOP-20_4.4x6.5mm_P0.65mm
Y1: 16MHz; CSTNE16M0V53Z000R0

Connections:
/+3V3: ADC1.48, ADC1.50, ADC1.52, C20.1, C21.1, C36.1, C38.1, C40.1, C41.1, C63.1, C64.1, R27.1, R28.1, U3.1, U6.2, U6.10
/+5V: C23.1, C24.1, C25.1, C42.1, C43.1, C48.1, C49.1, C50.1, C51.1, C55.1, C56.1, C57.1, C58.1, C59.1, C61.1, C65.1, C66.1, D7.1, D8.2, D9.2, J5.5, J6.2, R16.1, R24.2, U1.4, U1.6, U1.18, U4.4, U5.4, U5.20, U6.19
/ADC1299/AVDD: ADC1.1, ADC1.3, ADC1.5, ADC1.7, ADC1.9, ADC1.11, ADC1.13, ADC1.15, ADC1.19, ADC1.21, ADC1.22, ADC1.54, ADC1.56, ADC1.59, C10.1, C12.2, C14.2, C17.2, C28.1, C30.1, C32.1, C33.1, C34.1, C35.1, C37.1, C39.1, R22.2, SW3.1, SW4.1, SW5.1, SW6.1, SW7.1, SW8.1, SW9.1, SW10.1, SW11.1, U2.4, U3.2
/ADC1299/VCAP1: ADC1.28, C16.1, J15.1
/ADC1299/VREFP: ADC1.24, C13.2, J14.2
/Arduino Nano/+3V3: C54.1, U5.17
/Arduino Nano/RX: R18.1, U5.1
/Arduino Nano/SS_TX: R20.1, R21.2, U1.13
/Arduino Nano/TX: R17.1, U5.5
/Arduino Nano/VUSB: C52.1, C53.1, D7.2, F2.1
/GND: ADC1.20, ADC1.23, ADC1.25, ADC1.31, ADC1.32, ADC1.33, ADC1.41, ADC1.49, ADC1.51, ADC1.53, ADC1.57, ADC1.58, ADC1.60, C9.2, C10.2, C12.1, C13.1, C14.1, C15.1, C16.2, C17.1, C18.1, C19.2, C20.2, C21.2, C22.2, C23.2, C24.2, C25.2, C26.2, C27.2, C28.2, C29.2, C30.2, C31.2, C32.2, C33.2, C34.2, C35.2, C36.2, C37.2, C38.2, C39.2, C40.2, C41.2, C42.2, C43.2, C44.2, C45.2, C46.2, C47.2, C48.2, C49.2, C50.2, C51.2, C52.2, C53.2, C54.2, C55.2, C56.2, C57.2, C58.2, C59.2, C61.2, C62.2, C63.2, C64.2, C65.2, C66.2, D4.1, D5.1, D6.1, J2.5, J2.6, J4.1, J5.4, J6.6, J7.1, J10.1, J12.1, J14.1, J15.2, J16.1, PB1.1, PB1.2, R12.2, R13.1, R14.1, R15.1, R19.2, R20.2, R28.2, U1.3, U1.5, U1.21, U2.3, U2.5, U2.6, U3.3, U4.3, U4.5, U4.6, U5.7, U5.18, U5.21, U5.25, U5.26, U6.11, Y1.2
/HC05_RX: J5.3, U1.12
/HC05_TX: J5.2, R21.1
/MISO_3V3: ADC1.43, U6.3
/MISO_5V: J6.1, U1.16, U6.18
/MOSI_3V3: ADC1.34, U6.4
/MOSI_5V: J6.4, U1.15, U6.17
/SCLK_3V3: ADC1.40, U6.5
/SCLK_5V: J6.3, U1.17, U6.16
/START_3V3: ADC1.38, J12.2, U6.6
/START_5V: U1.11, U6.15
/VIN: C26.1, C27.1, C29.1, C31.1, C44.1, C45.1, C46.1, C47.1, D3.1, Q1.2, U2.1, U2.2, U4.1, U4.2
/VIN_RAW: F1.2, J4.2, J7.2
/~CS_3V3: ADC1.39, J10.2, R27.2, U6.1
/~CS_5V: U1.2, U6.20
/~DRDY_3V3: ADC1.47, J16.2, U6.7
/~DRDY_5V: U1.10, U6.14
/~PWDN_3V3: ADC1.35, U6.9
/~PWDN_5V: U1.9, U6.12
/~RESET_3V3: ADC1.36, U6.8
/~RESET_5V: C60.2, C62.1, J6.5, PB1.3, PB1.4, R16.2, U1.29, U6.13
unnamed: ADC1.2, C1.1, R3.1
unnamed: ADC1.4, C2.1, R4.1
unnamed: ADC1.6, C3.1, R5.1
unnamed: ADC1.8, C4.1, R6.1
unnamed: ADC1.10, C5.1, R7.1
unnamed: ADC1.12, C6.1, R8.1
unnamed: ADC1.14, C7.1, R9.1
unnamed: ADC1.16, C8.1, R10.1
unnamed: ADC1.17, C1.2, C2.2, C3.2, C4.2, C5.2, C6.2, C7.2, C8.2, R11.1
unnamed: ADC1.26, C9.1
unnamed: ADC1.30, C19.1
unnamed: ADC1.42, R12.1
unnamed: ADC1.44, R15.2
unnamed: ADC1.45, R14.2
unnamed: ADC1.46, R13.2
unnamed: ADC1.55, C15.2, C18.2
unnamed: C22.1, U1.20
unnamed: C60.1, U5.2
unnamed: D3.2, Q1.1, R19.1
unnamed: D4.2, R22.1
unnamed: D5.2, R23.1
unnamed: D6.2, R24.1
unnamed: D8.1, R25.1
unnamed: D9.1, R26.1
unnamed: F1.1, Q1.3
unnamed: F2.2, J2.1
unnamed: J1.1, SW3.3
unnamed: J2.2, U5.16
unnamed: J2.3, U5.15
unnamed: J3.1, SW4.3
unnamed: J8.1, SW5.3
unnamed: J9.1, SW6.3
unnamed: J11.1, SW7.3
unnamed: J13.1, SW8.3
unnamed: J17.1, SW9.3
unnamed: J18.1, SW10.3
unnamed: J19.1, SW11.3
unnamed: R3.2, SW3.2
unnamed: R4.2, SW4.2
unnamed: R5.2, SW5.2
unnamed: R6.2, SW6.2
unnamed: R7.2, SW7.2
unnamed: R8.2, SW8.2
unnamed: R9.2, SW9.2
unnamed: R10.2, SW10.2
unnamed: R11.2, SW11.2
unnamed: R17.2, U1.31
unnamed: R18.2, U1.30
unnamed: R23.2, U1.1
unnamed: R25.2, U5.23
unnamed: R26.2, U5.22
unnamed: U1.7, Y1.3
unnamed: U1.8, Y1.1

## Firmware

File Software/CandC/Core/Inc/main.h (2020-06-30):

/* USER CODE BEGIN Header */
/**
  ******************************************************************************
  * @file           : main.h
  * @brief          : Header for main.c file.
  *                   This file contains the common defines of the application.
  ******************************************************************************
  * @attention
  *
  * <h2><center>&copy; Copyright (c) 2020 STMicroelectronics.
  * All rights reserved.</center></h2>
  *
  * This software component is licensed by ST under BSD 3-Clause license,
  * the "License"; You may not use this file except in compliance with the
  * License. You may obtain a copy of the License at:
  *                        opensource.org/licenses/BSD-3-Clause
  *
  ******************************************************************************
  */
/* USER CODE END Header */

/* Define to prevent recursive inclusion -------------------------------------*/
#ifndef __MAIN_H
#define __MAIN_H

#ifdef __cplusplus
extern "C" {
#endif

/* Includes ------------------------------------------------------------------*/
#include "stm32f4xx_hal.h"

/* Private includes ----------------------------------------------------------*/
/* USER CODE BEGIN Includes */

/* USER CODE END Includes */

/* Exported types ------------------------------------------------------------*/
/* USER CODE BEGIN ET */

/* USER CODE END ET */

/* Exported constants --------------------------------------------------------*/
/* USER CODE BEGIN EC */

/* USER CODE END EC */

/* Exported macro ------------------------------------------------------------*/
/* USER CODE BEGIN EM */

/* USER CODE END EM */

void HAL_TIM_MspPostInit(TIM_HandleTypeDef *htim);

/* Exported functions prototypes ---------------------------------------------*/
void Error_Handler(void);

/* USER CODE BEGIN EFP */

/* USER CODE END EFP */

/* Private defines -----------------------------------------------------------*/
#define Ring_AD_Pin GPIO_PIN_0
#define Ring_AD_GPIO_Port GPIOC
#define Middle_ADC_Pin GPIO_PIN_1
#define Middle_ADC_GPIO_Port GPIOC
#define Index_ADC_Pin GPIO_PIN_2
#define Index_ADC_GPIO_Port GPIOC
#define Thumb_ADC_Pin GPIO_PIN_3
#define Thumb_ADC_GPIO_Port GPIOC
#define VSUPPLY_ADC_Pin GPIO_PIN_0
#define VSUPPLY_ADC_GPIO_Port GPIOA
#define Thumb_Pin GPIO_PIN_6
#define Thumb_GPIO_Port GPIOA
#define Index_Pin GPIO_PIN_7
#define Index_GPIO_Port GPIOA
#define Pinky_ADC_Pin GPIO_PIN_4
#define Pinky_ADC_GPIO_Port GPIOC
#define Wrist_ADC_Pin GPIO_PIN_5
#define Wrist_ADC_GPIO_Port GPIOC
#define Middle_Pin GPIO_PIN_0
#define Middle_GPIO_Port GPIOB
#define Ring_Pin GPIO_PIN_1
#define Ring_GPIO_Port GPIOB
#define Pinky_Pin GPIO_PIN_12
#define Pinky_GPIO_Port GPIOD
#define Wrist_Pin GPIO_PIN_13
#define Wrist_GPIO_Port GPIOD
/* USER CODE BEGIN Private defines */

/* USER CODE END Private defines */

#ifdef __cplusplus
}
#endif

#endif /* __MAIN_H */

/************************ (C) COPYRIGHT STMicroelectronics *****END OF FILE****/

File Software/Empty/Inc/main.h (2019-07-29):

/* USER CODE BEGIN Header */
/**
  ******************************************************************************
  * @file           : main.h
  * @brief          : Header for main.c file.
  *                   This file contains the common defines of the application.
  ******************************************************************************
  ** This notice applies to any and all portions of this file
  * that are not between comment pairs USER CODE BEGIN and
  * USER CODE END. Other portions of this file, whether 
  * inserted by the user or by software development tools
  * are owned by their respective copyright owners.
  *
  * COPYRIGHT(c) 2019 STMicroelectronics
  *
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
  ******************************************************************************
  */
/* USER CODE END Header */

/* Define to prevent recursive inclusion -------------------------------------*/
#ifndef __MAIN_H
#define __MAIN_H

#ifdef __cplusplus
extern "C" {
#endif

/* Includes ------------------------------------------------------------------*/
#include "stm32f4xx_hal.h"
#include "stm32f4xx_hal.h"

/* Private includes ----------------------------------------------------------*/
/* USER CODE BEGIN Includes */

/* USER CODE END Includes */

/* Exported types ------------------------------------------------------------*/
/* USER CODE BEGIN ET */

/* USER CODE END ET */

/* Exported constants --------------------------------------------------------*/
/* USER CODE BEGIN EC */

/* USER CODE END EC */

/* Exported macro ------------------------------------------------------------*/
/* USER CODE BEGIN EM */

/* USER CODE END EM */

/* Exported functions prototypes ---------------------------------------------*/
void Error_Handler(void);

/* USER CODE BEGIN EFP */

/* USER CODE END EFP */

/* Private defines -----------------------------------------------------------*/
#define CS_I2C_SPI_Pin GPIO_PIN_3
#define CS_I2C_SPI_GPIO_Port GPIOE
#define PC14_OSC32_IN_Pin GPIO_PIN_14
#define PC14_OSC32_IN_GPIO_Port GPIOC
#define PC15_OSC32_OUT_Pin GPIO_PIN_15
#define PC15_OSC32_OUT_GPIO_Port GPIOC
#define PH0_OSC_IN_Pin GPIO_PIN_0
#define PH0_OSC_IN_GPIO_Port GPIOH
#define PH1_OSC_OUT_Pin GPIO_PIN_1
#define PH1_OSC_OUT_GPIO_Port GPIOH
#define OTG_FS_PowerSwitchOn_Pin GPIO_PIN_0
#define OTG_FS_PowerSwitchOn_GPIO_Port GPIOC
#define PDM_OUT_Pin GPIO_PIN_3
#define PDM_OUT_GPIO_Port GPIOC
#define B1_Pin GPIO_PIN_0
#define B1_GPIO_Port GPIOA
#define I2S3_WS_Pin GPIO_PIN_4
#define I2S3_WS_GPIO_Port GPIOA
#define SPI1_SCK_Pin GPIO_PIN_5
#define SPI1_SCK_GPIO_Port GPIOA
#define SPI1_MISO_Pin GPIO_PIN_6
#define SPI1_MISO_GPIO_Port GPIOA
#define SPI1_MOSI_Pin GPIO_PIN_7
#define SPI1_MOSI_GPIO_Port GPIOA
#define LCDTP_CS_Pin GPIO_PIN_4
#define LCDTP_CS_GPIO_Port GPIOC
#define LCDTP_IRQ_Pin GPIO_PIN_5
#define LCDTP_IRQ_GPIO_Port GPIOC
#define BL_PWM_Pin GPIO_PIN_0
#define BL_PWM_GPIO_Port GPIOB
#define BOOT1_Pin GPIO_PIN_2
#define BOOT1_GPIO_Port GPIOB
#define CLK_IN_Pin GPIO_PIN_10
#define CLK_IN_GPIO_Port GPIOB
#define LCDTP_CLK_Pin GPIO_PIN_13
#define LCDTP_CLK_GPIO_Port GPIOB
#define LCDTP_DOUT_Pin GPIO_PIN_14
#define LCDTP_DOUT_GPIO_Port GPIOB
#define LCDTP_DIN_Pin GPIO_PIN_15
#define LCDTP_DIN_GPIO_Port GPIOB
#define LD4_Pin GPIO_PIN_12
#define LD4_GPIO_Port GPIOD
#define LD3_Pin GPIO_PIN_13
#define LD3_GPIO_Port GPIOD
#define I2S3_MCK_Pin GPIO_PIN_7
#define I2S3_MCK_GPIO_Port GPIOC
#define VBUS_FS_Pin GPIO_PIN_9
#define VBUS_FS_GPIO_Port GPIOA
#define OTG_FS_ID_Pin GPIO_PIN_10
#define OTG_FS_ID_GPIO_Port GPIOA
#define OTG_FS_DM_Pin GPIO_PIN_11
#define OTG_FS_DM_GPIO_Port GPIOA
#define OTG_FS_DP_Pin GPIO_PIN_12
#define OTG_FS_DP_GPIO_Port GPIOA
#define SWDIO_Pin GPIO_PIN_13
#define SWDIO_GPIO_Port GPIOA
#define SWCLK_Pin GPIO_PIN_14
#define SWCLK_GPIO_Port GPIOA
#define I2S3_SCK_Pin GPIO_PIN_10
#define I2S3_SCK_GPIO_Port GPIOC
#define I2S3_SD_Pin GPIO_PIN_12
#define I2S3_SD_GPIO_Port GPIOC
#define SWO_Pin GPIO_PIN_3
#define SWO_GPIO_Port GPIOB
#define Audio_SCL_Pin GPIO_PIN_6
#define Audio_SCL_GPIO_Port GPIOB
#define Audio_SDA_Pin GPIO_PIN_9
#define Audio_SDA_GPIO_Port GPIOB
#define MEMS_INT2_Pin GPIO_PIN_1
#define MEMS_INT2_GPIO_Port GPIOE
/* USER CODE BEGIN Private defines */

/* USER CODE END Private defines */

#ifdef __cplusplus
}
#endif

#endif /* __MAIN_H */

/************************ (C) COPYRIGHT STMicroelectronics *****END OF FILE****/

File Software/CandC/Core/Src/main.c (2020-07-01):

/* USER CODE BEGIN Header */
/**
  ******************************************************************************
  * @file           : main.c
  * @brief          : Main program body
  ******************************************************************************
  * @attention
  *
  * <h2><center>&copy; Copyright (c) 2020 STMicroelectronics.
  * All rights reserved.</center></h2>
  *
  * This software component is licensed by ST under BSD 3-Clause license,
  * the "License"; You may not use this file except in compliance with the
  * License. You may obtain a copy of the License at:
  *                        opensource.org/licenses/BSD-3-Clause
  *
  ******************************************************************************
  */
/* USER CODE END Header */

/* Includes ------------------------------------------------------------------*/
#include "main.h"

/* Private includes ----------------------------------------------------------*/
/* USER CODE BEGIN Includes */
#include <stdlib.h>
#include <stdio.h>
#include <string.h>
#include "DCT.h"
#include "svm_predict.h"

//#define PRINTING_MODEL
//#define PRINTING_COEFFS
#ifndef EPOCH_LENGTH_SAMPLES
  #define EPOCH_LENGTH_SAMPLES 256
#endif
#define CHARS_PER_SAMPLE 11
#define SVM_SCALE_FACTOR 100000
//#define EEG_SCALE_FACTOR 1
#define EEG_SCALE_FACTOR 100000
#define ADC_VREF 3.3
#define ADC_MAX_COUNT 4095
#define FEEDBACK_GAIN 6
/* USER CODE END Includes */

/* Private typedef -----------------------------------------------------------*/
/* USER CODE BEGIN PTD */

/* USER CODE END PTD */

/* Private define ------------------------------------------------------------*/
/* USER CODE BEGIN PD */
/* USER CODE END PD */

/* Private macro -------------------------------------------------------------*/
/* USER CODE BEGIN PM */

/* USER CODE END PM */

/* Private variables ---------------------------------------------------------*/
ADC_HandleTypeDef hadc1;
DMA_HandleTypeDef hdma_adc1;

TIM_HandleTypeDef htim3;
TIM_HandleTypeDef htim4;

UART_HandleTypeDef huart4;
DMA_HandleTypeDef hdma_uart4_rx;

/* USER CODE BEGIN PV */

/* USER CODE END PV */

/* Private function prototypes -----------------------------------------------*/
void SystemClock_Config(void);
static void MX_GPIO_Init(void);
static void MX_DMA_Init(void);
static void MX_ADC1_Init(void);
static void MX_TIM3_Init(void);
static void MX_TIM4_Init(void);
static void MX_UART4_Init(void);
/* USER CODE BEGIN PFP */
void open_hand(void);
void close_hand(void);
double convert_ADC_to_volts(uint32_t);
double ohms_law(double, double);
double moving_average(double*, int);
void user_pwm_setvalue(long, TIM_HandleTypeDef*, uint32_t);

/* USER CODE END PFP */

/* Private user code ---------------------------------------------------------*/
/* USER CODE BEGIN 0 */

unsigned char RX_data[EPOCH_LENGTH_SAMPLES * CHARS_PER_SAMPLE] = {0};
double parsed_epoch_data[EPOCH_LENGTH_SAMPLES] = {0};
Linear_SVM_Model SVM;
uint32_t adc_values[7];        /**< The ADC Values are saved here */
double thumb_current_history[10] = {0};
double index_current_history[10] = {0};
double middle_current_history[10] = {0};
double ring_current_history[10] = {0};
double pinky_current_history[10] = {0};
char is_blocked[6] = {0};
char is_open = 0;

int parse_buffer(void) {
	char delim[] = "\n";
	char *ptr = strtok((char*)RX_data, delim);
	int sample_number = 0;
	while(ptr != NULL)
	{
		long value = atol(ptr);
		if (SVM.complete) { // this should be svm.complete
			parsed_epoch_data[sample_number] = ((double)value) / EEG_SCALE_FACTOR;
		}
		else {
			parsed_epoch_data[sample_number] = ((double)value) / SVM_SCALE_FACTOR;
		}
		sample_number++;
		ptr = strtok(NULL, delim);
	}
	return sample_number;
}

void process_sample(double coeffs[]) {
    parse_buffer();
	// Process this epoch
	int number_of_samples = sizeof(parsed_epoch_data) / sizeof(double);

	dct_test(coeffs, parsed_epoch_data, number_of_samples);
#ifdef PRINTING_COEFFS
	//This is just printing
	for (int i = 0; i < number_of_samples; i++) {
		char data_string[CHARS_PER_SAMPLE] = {0};
		snprintf(data_string,  CHARS_PER_SAMPLE, "%010lf", coeffs[i]);
		HAL_UART_Transmit(&huart4, (unsigned char *)data_string, CHARS_PER_SAMPLE, 0xFFFF);
		HAL_UART_Transmit(&huart4, (unsigned char *)"\n\r", 3, 0xFFFF);
	}
#endif

}

#ifdef PRINTING_MODEL
void print_model(Linear_SVM_Model* model) {
	if (model->complete) {
		char weight_str[255] = {0};
		HAL_UART_Transmit(&huart4, (unsigned char *)"Weights\n\r", 10, 0xFFFF);
		for (int i = 0; i < EPOCH_LENGTH_SAMPLES; i++) {
			snprintf(weight_str, 11, "%010ld", (long)(model->weight_vector[i]*1000));
			HAL_UART_Transmit(&huart4, (unsigned char *)weight_str, 11, 0xFFFF);
			HAL_UART_Transmit(&huart4, (unsigned char *)"\r\n", 3, 0xFFFF);
		}

		char scale_str[255] = {0};
		char offset_str[255] = {0};
		char dimension_str[255] = {0};
		snprintf(scale_str, 11, "%010ld", (long)(model->scale * 1000));
		snprintf(offset_str, 11, "%010ld", (long)(model->offset * 1000));
		snprintf(dimension_str, 11, "%010ld", (long)(model->dimension * 1000));

		HAL_UART_Transmit(&huart4, (unsigned char*)"Scale: ", 7, 0xFFFF);
		HAL_UART_Transmit(&huart4, (unsigned char*)scale_str, 11, 0xFFFF);
		HAL_UART_Transmit(&huart4, (unsigned char*)"\n\r", 3, 0xFFFF);

		HAL_UART_Transmit(&huart4, (unsigned char*)"Offset: ", 8, 0xFFFF);
		HAL_UART_Transmit(&huart4, (unsigned char*)offset_str, 11, 0xFFFF);
		HAL_UART_Transmit(&huart4, (unsigned char*)"\n\r", 3, 0xFFFF);

		HAL_UART_Transmit(&huart4, (unsigned char*)"Dimension: ", 11, 0xFFFF);
		HAL_UART_Transmit(&huart4, (unsigned char*)dimension_str, 11, 0xFFFF);
		HAL_UART_Transmit(&huart4, (unsigned char*)"\n\r", 3, 0xFFFF);
	}

}
#endif

void build_model(void) {
	parse_buffer();
	if (SVM.has_vector == 0) {
		/* Load the weight vector */
		int number_of_weights = sizeof(parsed_epoch_data) / sizeof(double);   // Get the number of coefficients in the weight vector
		double vect[number_of_weights];      // This is an array to hold the weights once converted to double from long
		for (int i = 0; i < number_of_weights; i++) {
			vect[i] = (parsed_epoch_data[i]); // Convert the weight to double then divide by the scale factor
		}
		//SVM->weight_vector = malloc(number_of_weights * sizeof(double));
		memcpy(SVM.weight_vector, vect, sizeof(vect));   // Store the scaled weights into the model, SVM.weight_vector is no longer NULL
		SVM.has_vector = 1;
	}
	else {
		/* Load the offset, scale and dimension */
		SVM.scale = (parsed_epoch_data[0]);
		SVM.offset = (parsed_epoch_data[1]);
		SVM.dimension = (parsed_epoch_data[2]);
		SVM.complete = 1;
		open_hand();
		HAL_Delay(250);
		close_hand();
#ifdef PRINTING_MODEL
		print_model(SVM);
#endif
	}
}

void HAL_UART_RxCpltCallback(UART_HandleTypeDef *huart) {
	if (SVM.complete) { //should be complete not not complete
		double coeffs[EPOCH_LENGTH_SAMPLES] = {0};
        process_sample(coeffs);
        double prediction = Linear_SVM_Predict(&SVM, coeffs);
        if (prediction < 0) {
        	open_hand();
        }
        else {
        	close_hand();
        }
	}
	else {        //This happens when we haven't got the model yet
		/* Get the model */
		build_model();
	}
	HAL_UART_Receive_IT(&huart4, RX_data, EPOCH_LENGTH_SAMPLES * CHARS_PER_SAMPLE); // Start listening. You now have 1 epoch to process this epoch
}
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

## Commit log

2019-07-30 Initial commit of task list
    [Task List.xlsx]
2019-08-01 Updates to task list, initial commit of pwm with serial program (working)
    [Task List.xlsx]
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2019-08-22 Initial commit of DAQ board. Unversioned a settings file from pwm_with_serial/.settings
    [DAQ Board.kicad_pcb, DAQ Board.sch]
2019-09-05 Initial commit of datasheets and ADC eval board
    [ADS1299 Eval Board.kicad_pcb, ADS1299 Eval Board.sch]
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2019-09-16 Removed old eval board schematic. Finished support circuitry for ADS1299-8
    [ADC1299.sch, ADS1299 Eval Board.kicad_pcb, ADS1299 Eval Board.sch, DAQ Board.sch]
2019-09-17 Added Arduino Nano and associated datasheets
    [ADC1299.sch, Arduino_Nano.sch, DAQ Board.sch]
2019-10-01 Updates to DAQ board
    [ADC1299.sch, Arduino_Nano.sch, DAQ Board.sch]
2019-10-13 DAQ board laid out, need to start routing
    [ADC1299.sch, Arduino_Nano.sch, DAQ Board.kicad_pcb, DAQ Board.sch]
2019-10-14 Started layout, added MCU datasheet
    [DAQ Board.kicad_pcb]
2019-10-15 Shrank the board, changed out PB, changed 9 pin header for a a shrouded one
    [ADC1299.sch, Arduino_Nano.sch, DAQ Board.kicad_pcb, DAQ Board.sch]
2019-10-15 Small changes
    [DAQ Board.kicad_pcb]
2019-10-17 About to start routing traces
    [DAQ Board.kicad_pcb]
2019-10-20 Kineses Board layout finished, about to start routing
    [DAQ Board.kicad_pcb, Kineses_Board.kicad_pcb, Kineses_Board.sch]
2019-10-20 Finished routing
    [Kineses_Board.kicad_pcb]
2019-10-20 Routing finished
    [Kineses_Board.kicad_pcb, Kineses_Board.sch]
2019-10-20 Changed 5V regulators for LDOs, changed datasheet for 100u tantalum cap
    [ADC1299.sch, Arduino_Nano.sch, DAQ Board.kicad_pcb]
2019-10-20 Routed new LDOs
    [DAQ Board.kicad_pcb]
2019-10-22 Updated pics, added more to hardware section
    [Kineses_Board.kicad_pcb]
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2019-10-23 Initial commit of gerber files
    [DAQ Board-B.Adhes.gbr, DAQ Board-B.CrtYd.gbr, DAQ Board-B.Cu.gbr, DAQ Board-B.Mask.gbr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]
2019-10-24 Added test points, initial commit of BoM
    [ADC1299.sch, BoM.xlsx, DAQ Board.kicad_pcb, DAQ Board.sch]
2019-10-28 Updated gerbers. Initial commit of interim Presentation
    [BOM_PCBWay.xlsx, Kineses_Board-B.Cu.gbr, Kineses_Board-B.Mask.gbr, Kineses_Board-B.Paste.gbr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]
2019-11-05 Report just about done
    [DAQ Board.sch]
2019-11-05 Initial commit of Interim Report - A Brain Computer Interface Controlled 3D Printed Prosthetic - Samuel Parker and Kaushik Mahata.docx, Gantt Chart.xlsx, and several photos
    [Gantt Chart.xlsx]
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2019-12-19 Many changes, mostly about rotating the board
    [BoM.xlsx, DAQ Board.kicad_pcb, DAQ Board.sch]
2019-12-27 fixed problem where RESET from FTDI chip was connected via cap to GND not RESET. Added 10u cap across reset PB.
    [ADC1299.sch, Arduino_Nano.sch, DAQ Board.kicad_pcb, DAQ Board.sch]
2019-12-27 moved some vias
    [DAQ Board.kicad_pcb]
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2019-12-27 Added pullup to ADS1299 CS pin
    [ADC1299.sch, DAQ Board.kicad_pcb]
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2019-12-27 Updated BoM
    [BoM.xlsx, DAQ Board.sch]
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2019-12-28 ran DRC
    [ADC1299.sch, DAQ Board.kicad_pcb]
2019-12-28 Generated Output Files
    [DAQ Board-B.Adhes.gbr, DAQ Board-B.Cu.gbr, DAQ Board-B.Fab.gbr, DAQ Board-B.Mask.gbr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]
2019-12-28 Made all silkscreen text the same direction
    [DAQ Board-F.SilkS.gbr]
2019-12-28 Removed a stub and moved some vias. Regenerated production docs
    [DAQ Board-B.Adhes.gbr, DAQ Board-B.CrtYd.gbr, DAQ Board-B.Cu.gbr, DAQ Board-B.Fab.gbr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]
2019-12-28 actually saving the file this time
    [DAQ Board.kicad_pcb]
2019-12-28 removed a few extra vias
    [DAQ Board-B.Adhes.gbr, DAQ Board-B.CrtYd.gbr, DAQ Board-B.Cu.gbr, DAQ Board-B.Fab.gbr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]
2019-12-28 removed some more vias
    [DAQ Board-B.Adhes.gbr, DAQ Board-B.CrtYd.gbr, DAQ Board-B.Cu.gbr, DAQ Board-B.Fab.gbr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]
2019-12-28 Initial commit of Classification and Contol Board
    [Classification and Contol Board.kicad_pcb, Classification and Contol Board.sch]
2019-12-28 Added SWD programming header
    [Classification and Contol Board.kicad_pcb, Classification and Contol Board.sch]
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2019-12-28 Added VReg and caps
    [Classification and Contol Board.sch]
2019-12-29 Finished STM32F407VGTx, working on comms
    [Classification and Contol Board.sch, Communications.sch, Control.sch, STM32F407VGTx.sch]
2019-12-29 Finished Schematic
    [Classification and Contol Board.sch, Communications.sch, Control.sch, STM32F407VGTx.sch]
2019-12-29 Added footprints for all caps
    [Classification and Contol Board.sch, Communications.sch, STM32F407VGTx.sch]
2019-12-29 Added footprints for everything
    [Classification and Contol Board.sch, Communications.sch, Control.sch, STM32F407VGTx.sch]
2019-12-29 removed some decoupling, started layout
    [Classification and Contol Board.kicad_pcb, Communications.sch, STM32F407VGTx.sch]
2019-12-29 made a square section, it's a bit big though
    [square.kicad_pcb]
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2019-12-29 About to start routing
    [Classification and Contol Board.kicad_pcb, Classification and Contol Board.sch, Communications.sch, Control.sch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]
2019-12-30 Started Routing
    [Classification and Contol Board.kicad_pcb, Communications.sch]
2020-01-02 Most signals routed, working on power now
    [Classification and Contol Board.kicad_pcb, Classification and Contol Board.sch, Communications.sch, Control.sch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]
2020-01-02 about to grid vias
    [Classification and Contol Board.kicad_pcb]
2020-01-02 Routing done
    [Classification and Contol Board.kicad_pcb]
2020-01-04 Added BoM for C&C board
    [BoM.xlsx]
2020-01-04 Finished BoM
    [BoM.xlsx]
2020-01-04 Removed second sheet
    [BoM.xlsx]
2020-01-04 Made Digikey BoM
    [BoM.xlsx]
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2020-01-20 Flipped the DC connector
    [Classification and Contol Board.kicad_pcb]
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2020-01-20 Small change to schematic
    [STM32F407VGTx.sch]
2020-01-30 Double checked DAQ BOM before giving to Jerry for assembly
    [BoM.xlsx]
2020-01-31 Added a heading to the In Box column
    [BoM.xlsx]
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2020-03-24 Adding ADC breakout
    [ADC1299.sch, Arduino_Nano.sch, BoM.xlsx, DAQ Board-B.Adhes.gbr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]
2020-03-24 Changed unused analog inputs to AVDD, removed mid supply voltage divider. Small routing change
    [DAQ Board-B.Adhes.gbr, DAQ Board-B.CrtYd.gbr, DAQ Board-B.Cu.gbr, DAQ Board-B.Fab.gbr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]
2020-03-24 Small clearance changes, silkscreen art added
    [DAQ Board-B.Adhes.gbr, DAQ Board-B.CrtYd.gbr, DAQ Board-B.Cu.gbr, DAQ Board-B.Fab.gbr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]
2020-03-24 Large routing change to increase zone to header clearance and added CLK test point
    [DAQ Board-B.Adhes.gbr, DAQ Board-B.CrtYd.gbr, DAQ Board-B.Cu.gbr, DAQ Board-B.Fab.gbr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]
2020-03-24 Removed pullup resistor on /CS. Reran production pdfs and plotted schematic
    [BoM.xlsx, DAQ Board-B.Adhes.gbr, DAQ Board-B.CrtYd.gbr, DAQ Board-B.Cu.gbr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]
2020-03-24 Pushed power connector back, created Production PDFs
    [Classification and Contol Board-B.Adhes.gbr, Classification and Contol Board-B.CrtYd.gbr, Classification and Contol Board-B.Cu.gbr, Classification and Contol B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]
2020-03-26 Small routing change, added extra silkscreen labels
    [BoM.xlsx, DAQ Board-B.Adhes.gbr, DAQ Board-B.CrtYd.gbr, DAQ Board-B.Cu.gbr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]
2020-03-26 ADC BREAKOUT ASSEMBLY TAG
    [BoM.xlsx, DAQ Board-B.Adhes.gbr, DAQ Board-B.CrtYd.gbr, DAQ Board-B.Cu.gbr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]
2020-04-01 Reran plotting the schematic
    [BoM.xlsx]
2020-04-01 DRC passes
    [Classification and Contol Board.kicad_pcb]
2020-04-01 Removed BT / USB switch, changed reset button switch so now it will be correct
    [Classification and Contol Board.kicad_pcb, Classification and Contol Board.sch, Communications.sch, Control.sch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]
2020-04-01 Minor changes, and plotted schematic
    [Classification and Contol Board.kicad_pcb, Communications.sch, STM32F407VGTx.sch]
2020-04-01 Ran the Gerbers, made fab layer look fab
    [Classification and Contol Board.kicad_pcb]
2020-04-01 Changed blue LED to green and added current limiting resistor
    [Classification and Contol Board.kicad_pcb, STM32F407VGTx.sch]
2020-04-01 Fixed schematic note regarding voltage divider ratio
    [Control.sch]
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2020-04-23 Changed hardware to make USB use USART2 to be binary compatible with Dev Board. Moved some components accordingly.
    [Classification and Contol Board.kicad_pcb, STM32F407VGTx.sch]
2020-04-23 BoM Updates, fixed D1 footprint from 0805 to 0603
    [BoM.xlsx, Classification and Contol Board.kicad_pcb, STM32F407VGTx.sch]
2020-04-23 CLASSIFICATION AND CONTROL BOARD PRODUCTION
    [Classification and Contol Board-B.Adhes.gbr, Classification and Contol Board-B.CrtYd.gbr, Classification and Contol Board-B.Cu.gbr, Classification and Contol B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]
2020-05-04 Green for in the bag
    [BoM.xlsx]
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2020-05-19 Added level shifter and Software Serial. About to generate netlist, and see how that messes with the PCB
    [ADC1299.sch, Arduino_Nano.sch, DAQ Board.sch]
2020-05-19 Seems to have imported ok
    [Arduino_Nano.sch, DAQ Board.kicad_pcb, DAQ Board.sch]
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2020-06-18 Fixed TX<->TX problem, edited a Photo.jpg
    [Communications.sch]
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
